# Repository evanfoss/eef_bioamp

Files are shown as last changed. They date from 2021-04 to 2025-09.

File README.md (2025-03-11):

# EEF_BioAmp

This project is a family of differential input amplifiers with single ended outputs for use in electrophysiology. 
They are all *not* rated for use on humans. Let me repeat do not connect this to a person. If you do I am not responsible.

This is a fork of my original work here: https://github.com/EPL-Engineering/epl_bioamp

There are a few versions

EEF BioAmp "Fancy" - (master branch)

EEF BioAmp "Cheap" - (cheap branch)

### EEF BioAmp "Fancy"
The "Fancy" version has every bell and whistle we reasonably expect a user to need for doing ABR, DP, and EKG. Often these users have multiple dedicated amplifiers and prefer to use more involved filtering so that EKG signals can be seperated from ABR and etc for example.
The feature set I have given it so far includes.
* Twinaxial BNC Input
* Coaxial BNC Output
* Gain of 1K/10K or Gain of 10K/100K
* LPF 3KHz/10KHz
* HPF 300Hz 
* Optional the HPF can be 300Hz/10Hz
* Optional Power Line Frequency Rejection (currently 60Hz but I may do 50Hz in the future)
* Optional EPL Subrack Power
* Optional Battery Power

Please Note: The HPF option and Power Line Rejection option are mutually exclusive because of front panel constraints. Likewise the EPL Subrack Power and Battery Power are mutually exclusive because of rear panel space constraints. 

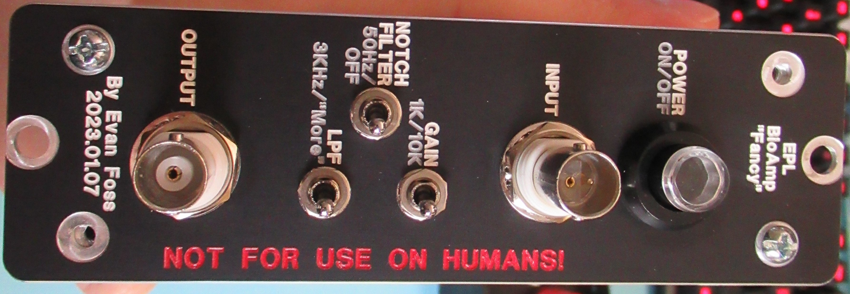
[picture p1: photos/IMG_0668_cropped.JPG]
Front panel of the bioamp.
|
|:---------------
|Pic1: A picture of a BioAmp front panel upclose enclosed in a subrack module.

|Circuitboards for the bioamp inside a chassis.
|:---------------
|Pic2: A picture of inside of an assembled BioAmp.

### EEF BioAmp "Cheap"

<this version is not maintaned currently>

The "Cheap" verion is designed to be pure minimalism. The idea was to have a lower cost version of the fancy that is just for ABR, DP, and EKG measurements. It's meant for our simple dedicated chambers where users exclusively do ABRs all day long with a single BioAmp and never adjust settings. The following is it's configuration.
* Twinaxial BNC Input
* Coaxial BNC Output
* Gain of 10K
* LPF 3KHz
* HPF 300Hz
* EPL Subrack Power
* Optional Power Line Frequency Rejection (currently just 60Hz but again I might add 50Hz later)

Please Note: The Power Line Frequency Rejection in some units is not user adjustable.

### EEF BioAmp "Breakout Pod"

This is shared between the "Cheap" and "Fancy" versions. Like both of them it is not for use on humans. 
It's features include the following.
* Twinaxial BNC Output
* 3 x 5 Way Binding Post Input
* 3 x 1.5mm Male Input (DIN 42802-1 Compatible Connectors)
* Holes on the sides for Mounting to Tables and etc.

The mounting holes are more important than they might sound. In a lot of our booths the EPL Subrack the EPL BioAmp sits in is on a shelf while the subject of the testing is on a sliding optical breadboard.

|5 breakout pods sitting next to each other.
|:---------------
|Pic2: A picture of 5 breakout pods.

# Development

### Toolchain

The development toolchain was as follows:

|Tool Name             | License        | Function
|:---------------      | :------------- | :-----------------
|<a href="https://octave.org/">Octave</a>                                                    | Open Source       | Scientific Programming Language used for calculations
|<a href="https://github.com/lepton-eda/lepton-eda">lepton-eda</a>                           | Open Source       | EDA (Electronic Design Automation) suite lepton-eda a fork of gEDA
|<a href="http://repo.hu/projects/pcb-rnd/">pcb-rnd</a>                                      | Open Source       | CAD (Computer Aided Design) tool for PCB (Printed Circuit Board) layout gEDA/PCB
|<a href="https://gerbv.github.io/">gerbv</a>                                                | Open Source       | Gerber viewer
|<a href="https://www.gnu.org/software/make/">GNU/Make</a>                                   | Open Source       | Toolchain automation
|<a href="https://www.frontpanelexpress.com/front-panel-designer">Front Panel Designer</a>   | Free as in Beer   | Front Panels Express Software

The toolchain automation uses the following commands:

|Command               | Implimented | Operation
|:---------------      | :------------- | :-----------------
|make all               | Yes           | edits Makefile
|make change            | Yes           | edits all projects schematics
|make simulation        | No            | runs spice simulation
|make graph             | Yes           | opens spice simulation graph(s)
|make mainmath          | Yes           | run the numbers for the filter values
|make notchmath         | Yes           | run the numbers for the notch filter option values
|make editmainmath      | Yes           | edit the code for the filter
|make editnotchmath     | Yes           | edit the code for the notch filter
|make pcb               | Yes           | edits bioamp main board pcb
|make pcb2              | Yes           | edits notchfilter option pcb 
|make pcb3              | Yes           | edits highpass filter option pcb
|make gerbv             | Yes           | opens gerber viewer of bioamp main pcb
|make gerbv2            | Yes           | opens gerber viewer of notchfilter pcb
|make gerbv3            | Yes           | opens gerber viewer of highpass filter option pcb

### Design

## Circuit Design

The diagram in Sch0 shows the overall design concept for the fancy version of the BioAmp. 

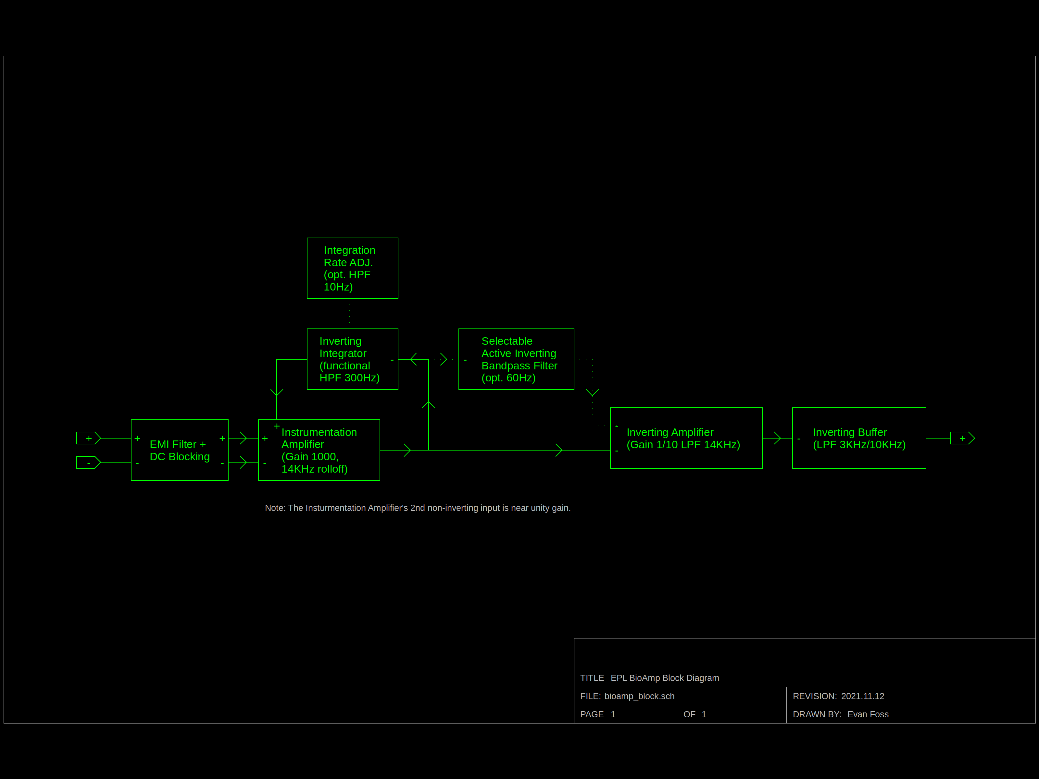
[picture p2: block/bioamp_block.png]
Block diagram of the fancy bioamp.
|
|:---------------
|Sch0: Block Diagram

The mainboard of the BioAmp is made up of the schematics Sch1 & Sch2. The optional Notch Filter board is just Sch3, and the optional highpass filter option is Sch4.

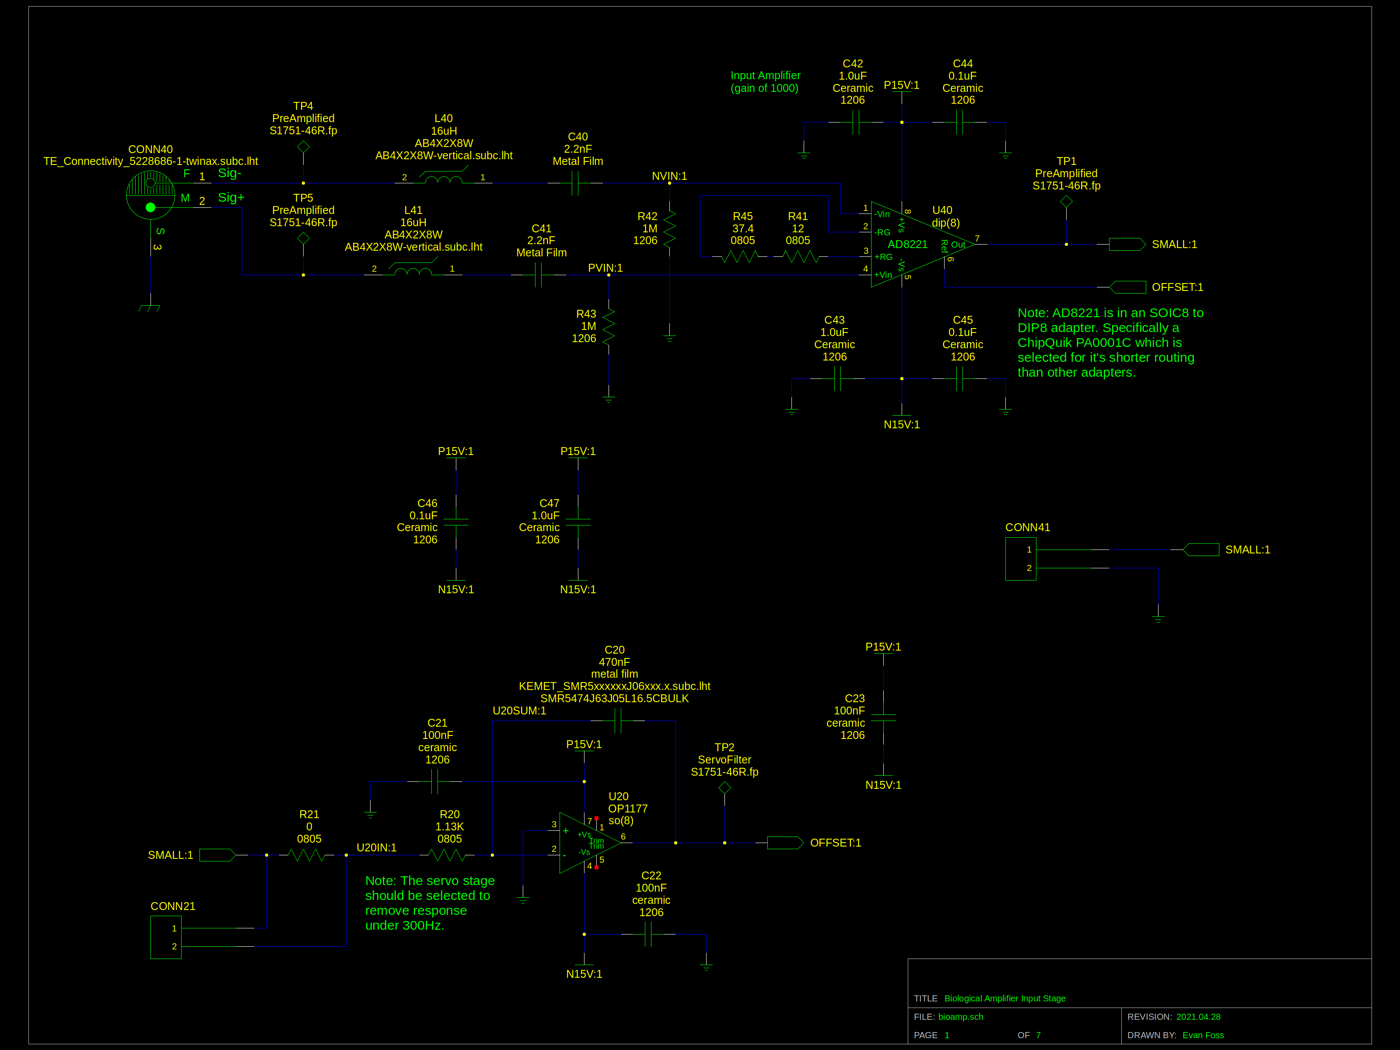
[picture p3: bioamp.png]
Bioamp input stage with integrator schematic.
|
|:---------------
|Sch1: BioAmp Input Stage

Sch1 shows the input filter composed of L40, L41, C40, C41, R42, and R43.

Sch1 also includes the insturmentation amplifier is U40, and it's gain limits it's frequency response. The gain for this stage is set by R45 + R41. It has the usual capacitors sprinkled around it for power supply decoupling.

U40 was selected for it's ability to operate at high gain with relatively low noise, and a level of input offset that could be overcome with an integrator. 

The inverting integrator which acts as a low pass filter is built around U20. R20 and C20 set the time constant for the integration. R21 and the jumper over it are for adjusting this lower limit if the highpass filter adjustment option is installed. 

U20 was selected for it's lower input bias current, low input offset voltage, and of course to drive a capacitive load. C20's composition was selected for low dielectric absorbtion. The same reasoning was used for C40, and C41. Dielectric absorbtion in C20 would lead the integrator to drifting and in C40 or C41 it would lead to the input stage having issues with input bias voltage.

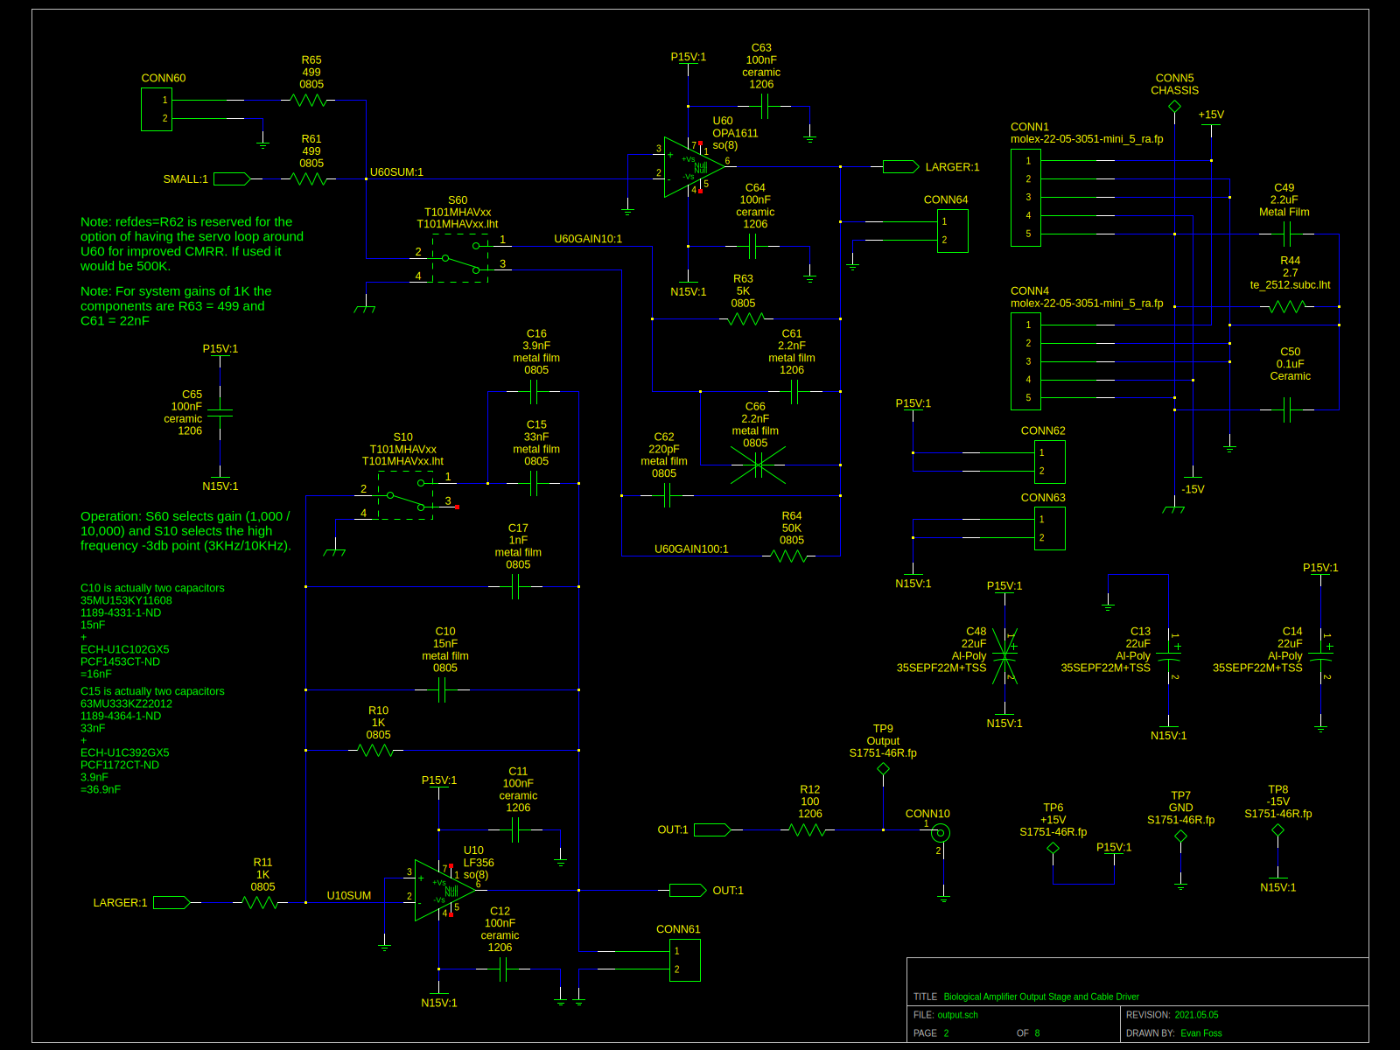
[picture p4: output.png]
Bioamp output stage schematic.
|
|:---------------
|Sch2: BioAmp Output Stage

Sch2 starts with the inverting amplifier that adds the rest of the gain required. It has 2 inputs. The 1st input is from the input stage on Sch1 and the 2nd is for the notch filter option. S20 selects the feedback RC pair (R63 & C61) or (R64 & C62). 

The use of the OPA1611 here is excessive considering it's performance characteristics but please see the note in "Supply Chain Issues". However it is very low noise in this application. 

In Sch2 we also have the final output stage which is built around U10. It is setup to just invert the signal at unit gain. The switch S10 adds added capacitence across the feedback resistor R10. Obviously R10 and R11 should match each other for this to work. C10+C17 put a limit on the frequency response. C16+C17 add more capacitence to lower the frequency response even more.

Once more to control noise the chassis ground is connected to the exterior of the switches S20 and S10 so that it can connect through them to the chassis.

Grounding gets complicated. Every amplifier in the chamber would work best if it was the only place were chassis ground and analog common were connected. That connection improves performance but you can't do that because of the ground loops it would add. That is why I now believe the over all enclosure (subrack/multiamplifier chassis) *or* the most sensitive/critical amplifier should be where that connection happens. Following that logic the next best thing we can do for each amplifier is to add an RC bridge between chassis and analog common. The 2.7 Ohm resistor is enough that it's not technically a "loop" and also small enough that the safety of a possible split where ever the chassis / common connection won't put the user in an unsafe situation. (but that should *never* *ever* happen!) Everyone repeat after me "I will never unground a chamber."

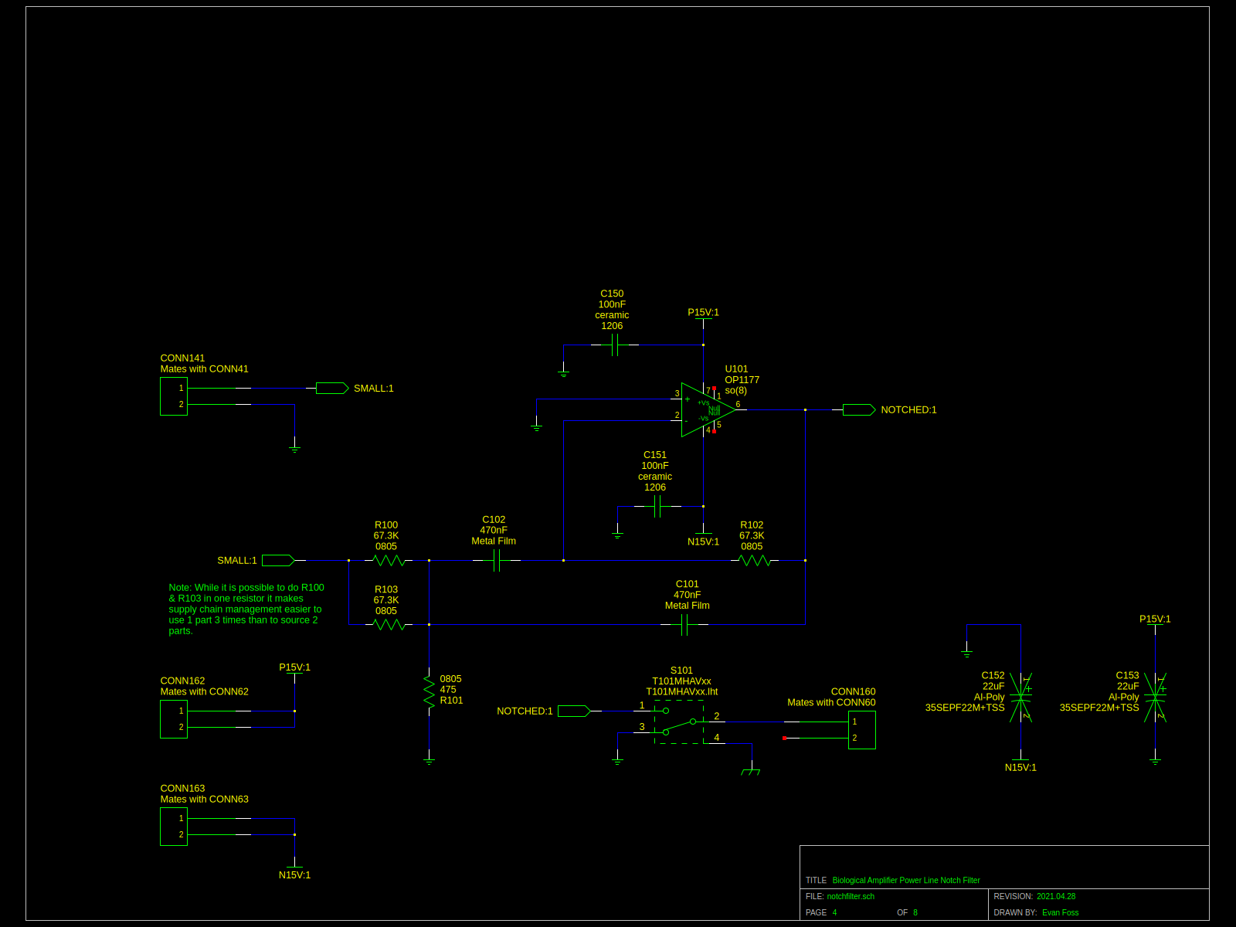
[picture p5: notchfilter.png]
Notch filter option schematic.
|
|:---------------
|Sch3: Notch filter option

The notch filter shown in Sch3 is built around U101. It works as an inverting unity gain filter. That way the inverted signal can be added back into the main device at cancel out the offending frequency. Normally this would cause phase issues but the frequency in question is 60Hz (or with changes 50Hz).

U101 was selected using the same criteria as U20 on Sch1 as a result the same part was selected. I should really say I picked this topology so I could use the same opamp and the same value for C101 and C102 as I did in C20. The catch is that C101 and C102 require a level of tollerance that C20 does not because the notch filter's performance is tied to the matching of these parts.

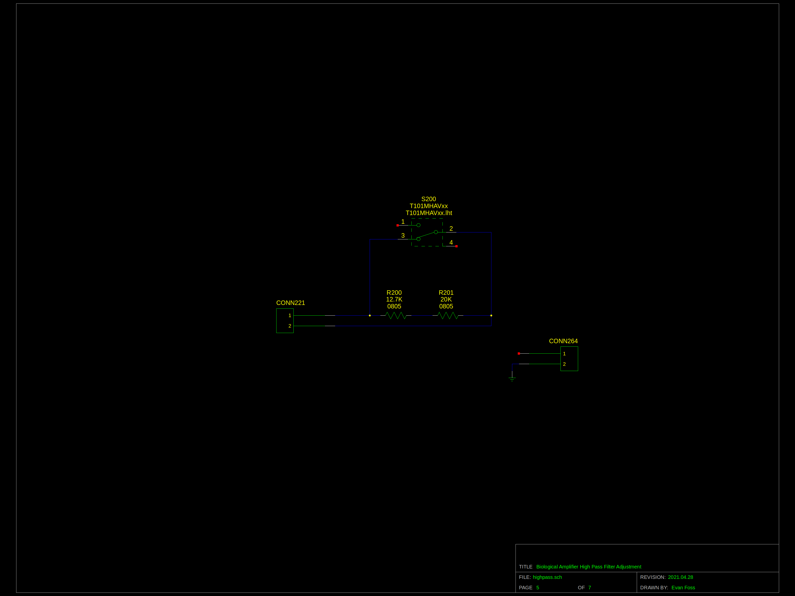
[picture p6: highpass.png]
Highpass filter lower frequency option schematic.
|
|:---------------
|Sch4: Highpass filter lower frequency option

Sch4 just optionally adds resistance in the integrator in Sch1 slowing down it's integration rate and lowering the input stage's highpass filter to 10Hz.

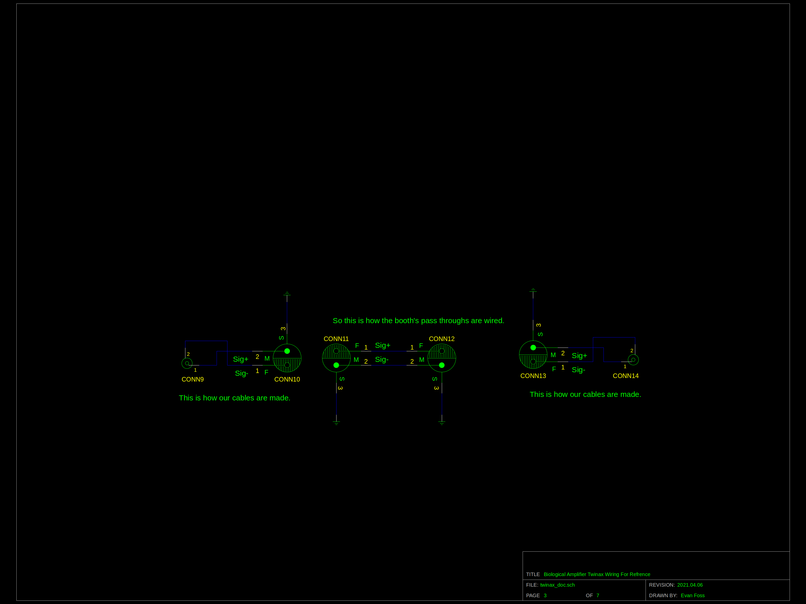
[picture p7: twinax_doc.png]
Schematic documenting the way twinaxial coax flips polarity from device to cable and back.
|
|:---------------
|Sch5: Twinaxial coax flips documented

Sch5 just helps you understand the polarity of the signal as it goes through the twinaxial wiring.

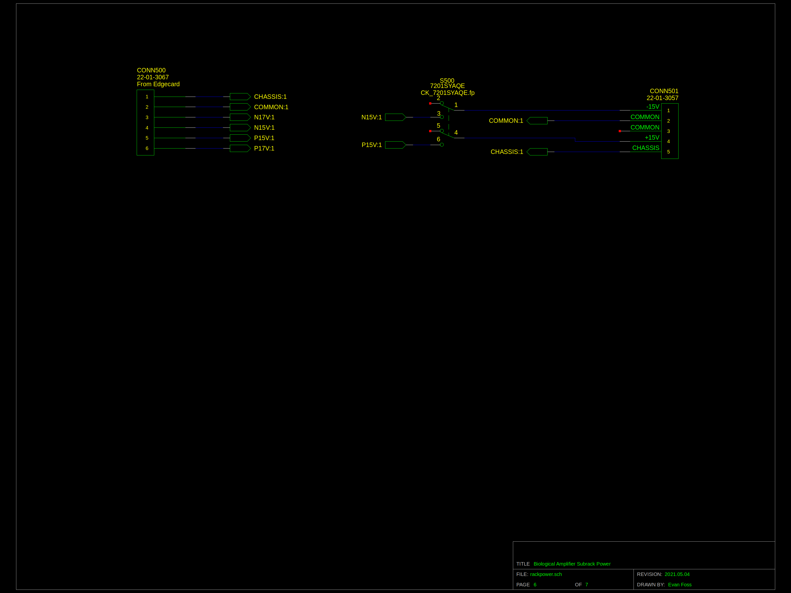
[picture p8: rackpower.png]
Rack based power schematic.
|
|:---------------
|Sch6: Rack based power option

Sch6 really is what it says.

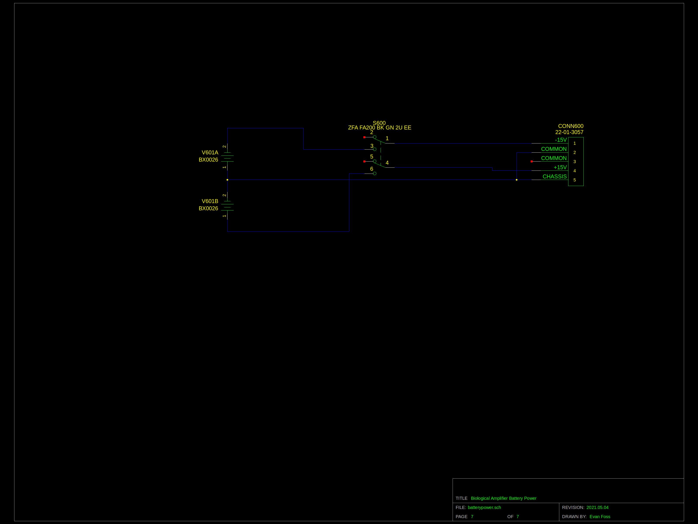
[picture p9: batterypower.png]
Battery based power schematic.
|
|:---------------
|Sch7: Battery based power option

Sch7 like Sch6 is exactly what it says. The one complication is that as this is the "only device" on this power supply it has to be where the analog common and chassis ground are connected.

## Printed Circuit Board Layout

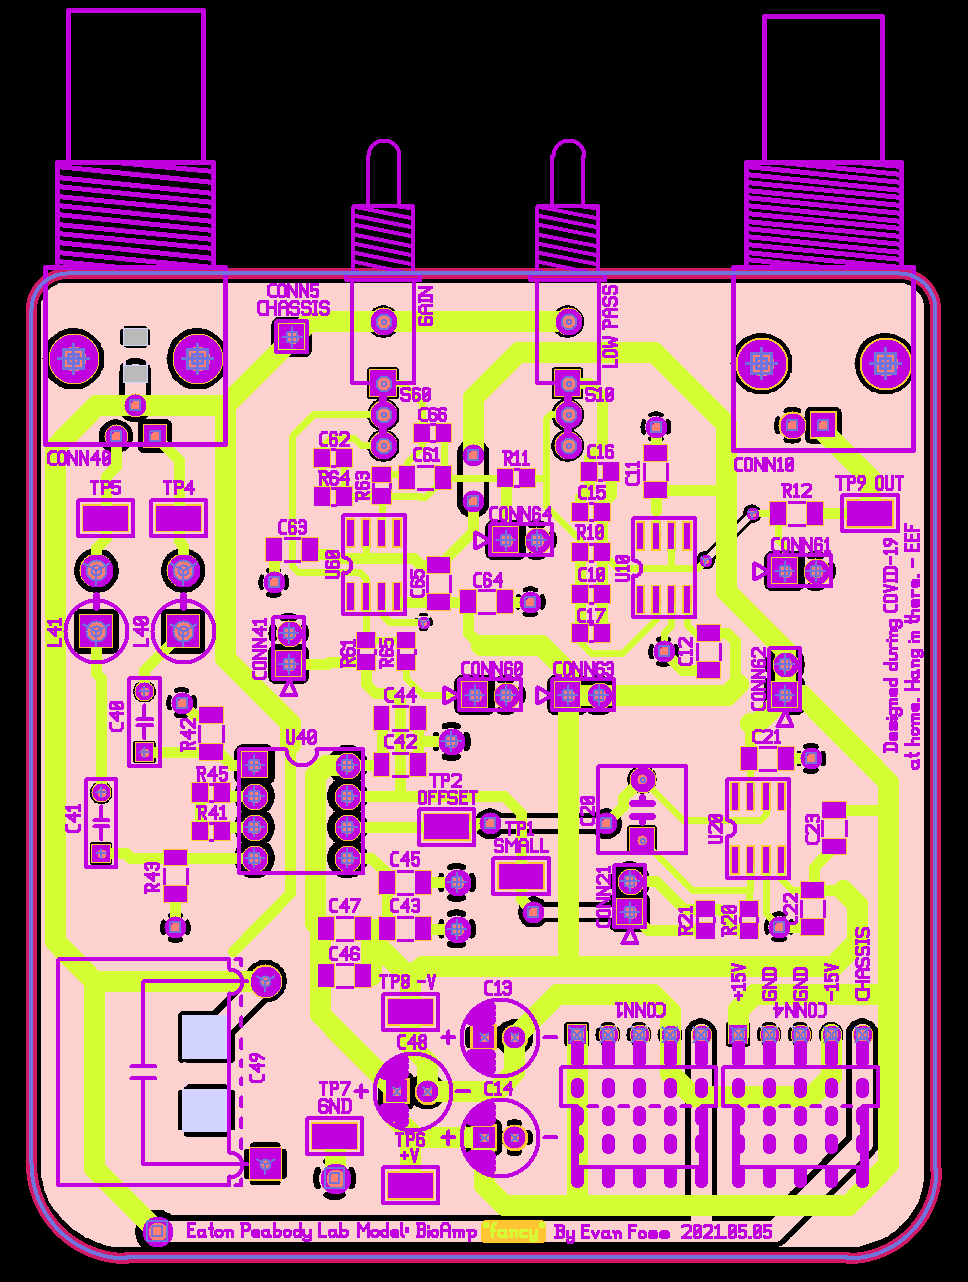
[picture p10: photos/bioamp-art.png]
Image of the main BioAmp PCB rendered by the gerber viewer in neon colors.
|
|:---------------
|PCB1: Image exported from the gerber viewer of the main BioAmp circuit board layout

One more thing about U40. Although it has yet to happen I believe this is the part most likely to be toasted by static discharge as it is the most directly connected to the user touchable connections. This is why it's on a small SOIC to DIP adapter. It is a method of reducing downtime from repairs. 

The layout was obviously designed to have the feedback paths as short as was reasonably possible. The decoupling capacitors were also kept close to the pins of the opamps they were meant to be near. Some effort was put into making sure the input side of the insturmentation amplifier was kept away from the rest of the design to avoid coupling anything over.

I sprinkled in a liberal number of test points so that repairs and debuging would be easier. 

The layout was drawn to be inside this size onvelope based on the packaging plan I had. For more on that see "Packaging".

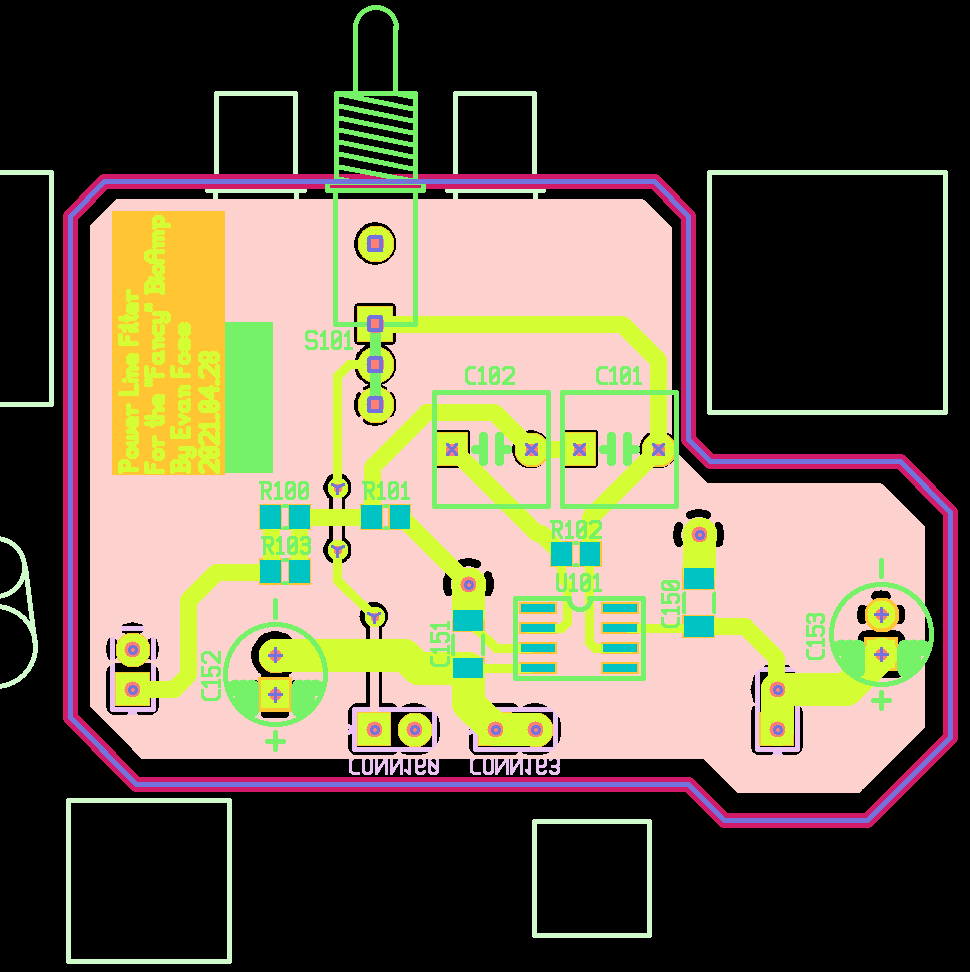
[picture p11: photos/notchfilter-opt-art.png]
Image of the Notch Filter PCB rendered by the gerber viewer in neon colors.
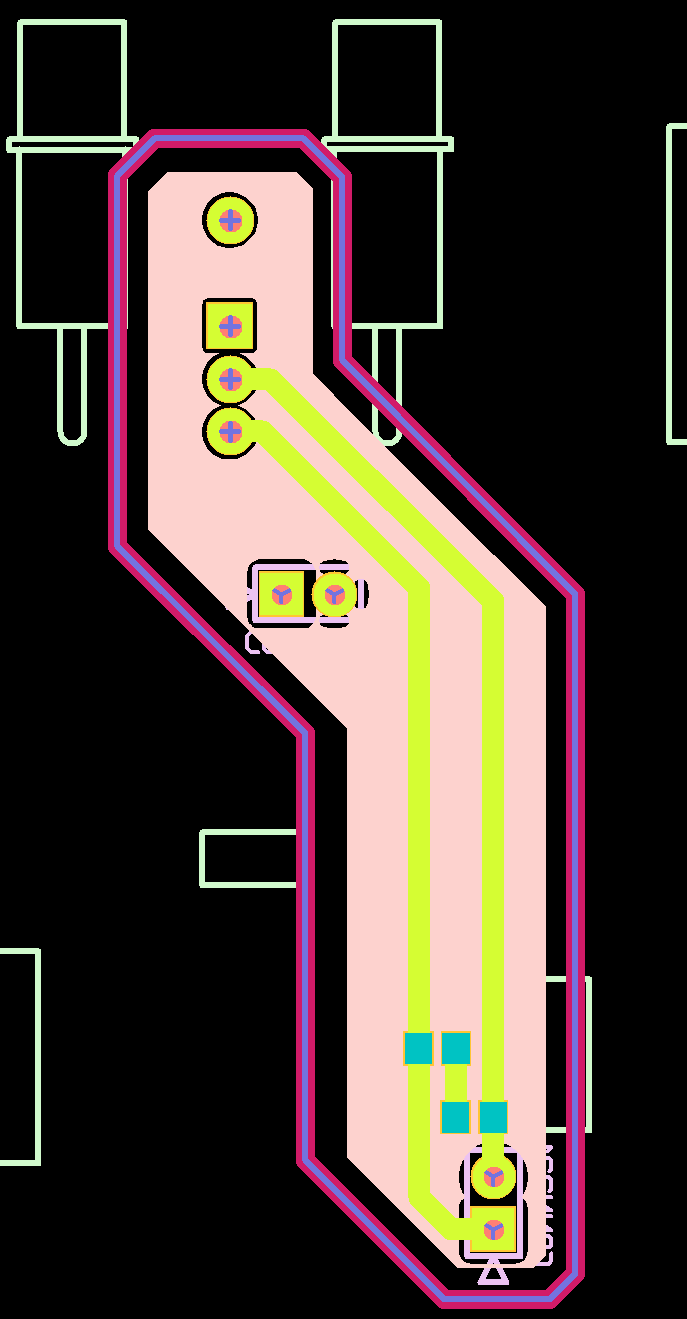
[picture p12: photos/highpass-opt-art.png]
Image of the High Pass Filter Adjustment Option PCB rendered by the gerber viewer in neon colors.
||
|:---------------                                   |:---------------
|PCB2: Notch Filter Option PCB Layout.                     |PCB3: Low Pass Filter Adjustment Option PCB Layout.

### Packaging

The BioAmp was designed with a few packaging options in mind. The image at the top of the README is of the front panel for a subrack module but it was also planned to be included in a standard 19" equipment/"server" rack package U1 size enclosure. The idea was to package it with the other hardware commonly used in the chamber for doing ABR (Auditory Brainstem Response) testing.

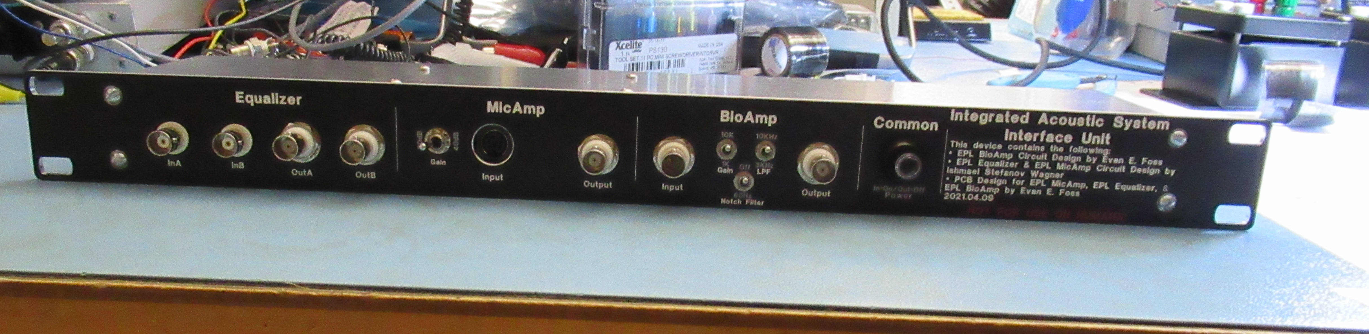
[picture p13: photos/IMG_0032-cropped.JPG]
Image of the combined front panel for the integrated bioamp with mic amp and equalizer.
|
|:---------------
|Pic3: Front panel of an integrated device with a <a href="https://github.com/evanfoss/eef_micamp">Mic Amp</a>, <a href="https://github.com/evanfoss/eef_equalizer">Equalizer</a> and BioAmp all in a U1 enclosure.

That said I prefer the subrack module packaging shown at the opening of the readme in Pic1 because of the other modules that fit neetly in the subrack.

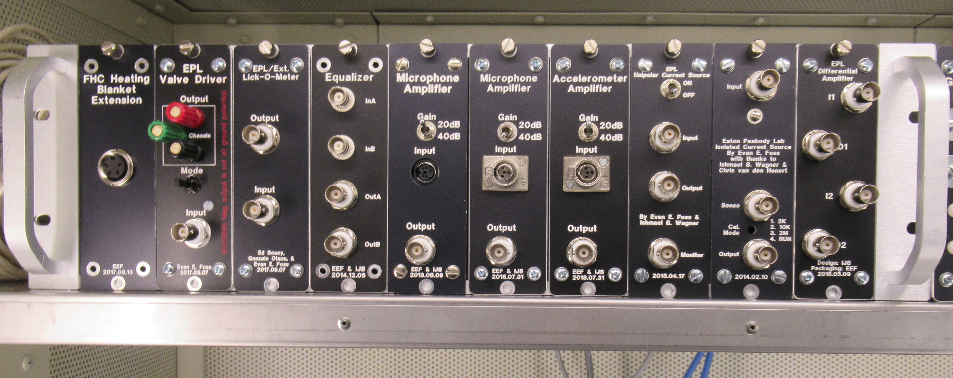
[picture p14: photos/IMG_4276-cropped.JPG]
Image of the subrack holding other modules that go in the rack
|
|:---------------
|Pic4: An array of just some of the many subrack modules that could be used in parallel to the BioAmp.

Outside of EPL of course this level of flexibility is in low demand.

The other big demand is of course battery powered operation. Now I frown on it because of the environmental footprint of batteries but there is a rear panel design that is included in the project files. Some thought went into the selection of the battery holder to make ease of changing the batteries without opening the cover easier. I find those little vinyl enclosed snap on 9V connectors unpleasant. The holder I selected costs a lot more but it works very well, the covers are hard to loose, and in most cases they make it impossible to put the batteries in backwards. 

The power button assembly was picked both because the on/off state was clearly visible without power but also because some experiments require low to zero illumination so power indicator lights are frowned appoon. I had a project with optogenetics and a blue power indicator in a commericially made device was causing trouble.

The breakout pod (Pic2) was designed in because many users require the chamber table to be at a distance from the equipment rack or for ergonomic reasons they need a chamber to have a pull out tray. So connecting the electrodes to the BioAmp front panel directly was not advisable.

### Manufacturing

Initial prototypes were made with hand soldering under a microscope. However I prefer to build these in batches which makes using solder paste nessisary. 

#### Reflow Soldering

With the switch to reflow soldering I had to switch to solder paste. Because solder paste has to be washable in this case the flux was going to dry out and I worried about the fine metal balls in the suspension were going to become a safety concern. This required the change to lead free solder to reduce exposure risk.

This is my current assembly process:

0. Verify that all parts are on hand including front panel
1. Stencil on solder paste
2. Apply SMT components
3. Warm the PCBA on a hot plate
4. Reflow PCBA
5. Ramp PCBA temperature down
6. Solder all through hole components except the switches and connectors
7. Insert switches and connectors and fasten them to the front panel (finger tight)
8. Solder switches and connectors
9. Detach front panel from PCBA
10. Wash PCBA and front panel seperatly
11. Check PCBA under microscope and record assembly with pictures
12. Assemble PCBA into chassis and test

|Populated ciruitboards for the bioamp.
|:---------------
|Pic5: Populated BioAmp main circuit board and notch filter option board on the right.

#### Supply Chain Issues

The Input stage IC AD8221 was selected before the COVID-19 pandemic and tarif issues made the supply chain for it an issue for me. The higher quality bin of the part (lower input offset rating) has at times been hard to keep instock. Likewise the capacitors used for limiting bandwidth in the stages of Sch2 are also an issue but I resolved that by adding pads for other packages in parallel.

The performance of the device in it's first prototypes (late 2020/early 2021) and the later itterations have drifted a bit. I believe this maybe do to variations in the process control of some parts. This is why the 10KHz LPF (Low Pass Filter) option is now marked as "More". I don't like it but as this feature is almost never used by 90% of users it for more than debugging test chamber noise restoring this to a known 10KHz is not a priority.

The OPA1611 was used because it was thought at the time that it would be used in later itterations of the MicAmp and that consolidation of the parts lists would help make stocking parts easier. In reality the testing of that which was concurrent with the testing of this project showed that it was a bad idea but the part is stocked now. It would have been nice if TI had not ceased production of the LME49710 so both designs could have used that part. *grumbles*

The notch filter requires on obscure part 67.3K Ohm resistors ideally in 1% or better tollerance. I resolved this issue by buying in large quantity.

To simplify the front panel design and supply chain issues I used the same model switch for everything.

The front panel twinaxial connector that is PCB mount and right angle is no longer manufactured. However it is still commonly available on the surplus market. The non-PCB mount version is also still common so you can buy those and solder wires to the PCB.

Finally some readers might notice that I used 22uF aluminum polymer capacitors instead of tantalum or ceramic. I stopped using tantalum and most ceramic because of the conditions around <a href="https://www.wbur.org/npr/1152893248/red-cobalt-congo-drc-mining-siddharth-kara">mining used in their production.</a> Ceramic capacitors were also avoided in many locations because of their microphonic effects <a href="https://product.tdk.com/system/files/contents/faq/capacitors-0031/singing_capacitors_piezoelectric_effect.pdf">caused by piezoelectric effects.</a>

### Validation

Validation was done by me at home with a homemade attenuator and my HP35665A and then repeated independently by Ishmael S. W. at EPL using the shop PXI and it's PXI4461 DAQ card before the BioAmp was released to the users. The first 3 or 4 users were also told to repeate the tests of frequency reponse and gain and found it proper for use in ABR (auditory brainstem response) measurement. For every unit I have made since these tests have been repeated with the HP35665A and cross checked against the original results for consistancy. Later it was suspected by me that the 10KHz option might infact be landing lower than 10KHz and so the feature was depreciated to "More" on the control panel. I bought a brand new Keysight U1733P and tested all the capacitors etc in one unit but could not find a suitable drift in component value to explain it. I had thought the soldering process revisions might be causing values to drift. More on this in the heading "Future".

### Testing

The use of an attenuator is required with the HP35665A as the input voltage range is so small all direct output settings from the DSA (Dynamic Signal Analyzer) would be too large. The attenuator's issues could actually be the cause of the LPF 10Hz issue.

Of the dozen or so units I made only a few were notably out of spec to the point where the capacitors (often tolleranced at 2% or better) needed to be swapped to meet requirements. This most commonly happened in the 60Hz notch filter where the parts exact rating doesn't matter as much as their matching which is harder to assure without an unreasonably high BOM price.

### Maintence and Errata

* 2021 - One unit destroyed when the user installed the batteries backwards frying most of the IC's inside. Additional labeling was added to the sides indicating battery alignment.
* 2022 - Added extra footprint for alternative package size C66 to replace C61
* 2025.03.10 - 3 Units (1 @ EPL, 1 @ _Unanmed_Biotech_Startup_, 1 @ Baylor) stopped operating until they were powered off and their inputs shorted temporarily.  Writing this documentation caused me to catch that I had listed the wrong composition for C40 & C41 in the BOM. Looking at that made me realize that the lockup issue was likely caused by those parts accumulating a charge. Normally the impedance to the refrence electrode would be on the order of 20K Ohms which should keep it discharged but I suspect over time charge is allowed to accumulate. I have a suggested correction. I would prefer 1.1nF instead of 1.2nF (1.1nF would hold the -3dB point @ 7.2343 Hz vs 1.2nF which puts it at 6.6315 Hz) however 1.1nF parts are not commonly available.

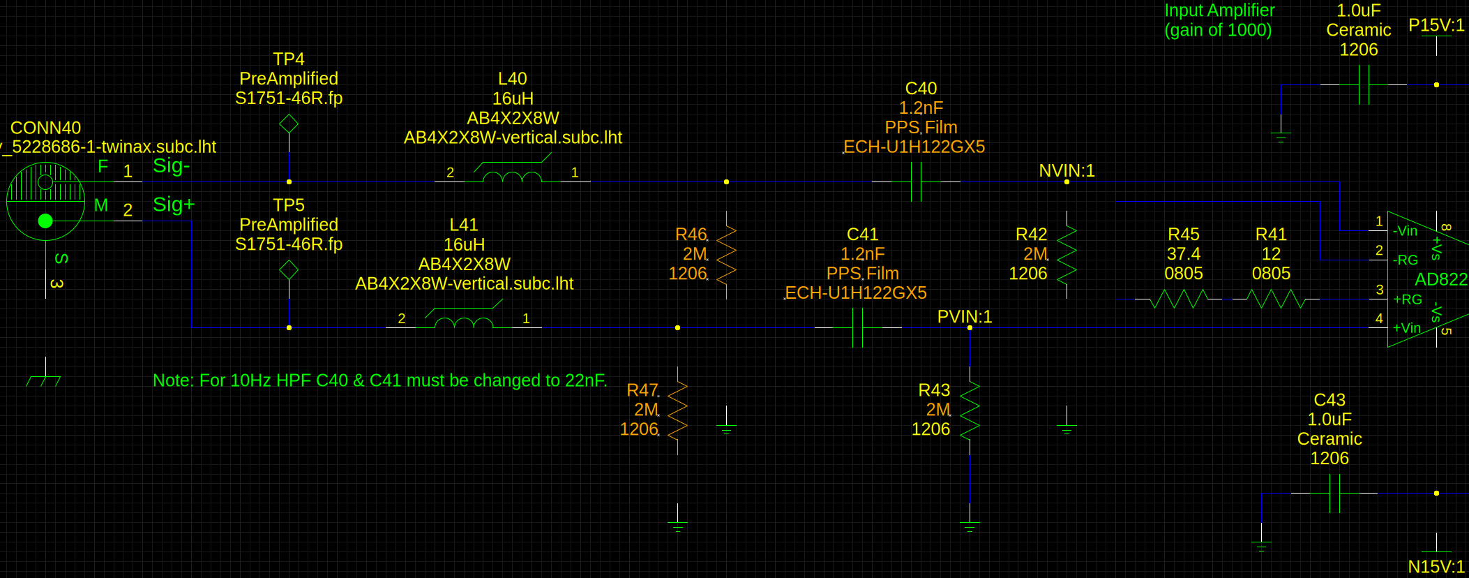
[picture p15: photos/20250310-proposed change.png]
revised schematic
|
|:---------------
|ALT1: I highlighted the changes. I am suggesting adding 2 more resistors before the input filter capacitors but after the inductors and changing the capacitors to PPS film (1.2nF) and the resistors 2M Ohm.

   Or we could just tell users to leave the + electrode in the 5 way - binding post top or vice versa between uses. As all three incidents happened multiple years into use this seems excessive.
   Another good option is to give users a small block of antistatic foam to squeeze between the 5 way binding posts and to tell them to insert the needles into that between uses.

* 2025.03.11 - I noticed there were some parts that I have never deliberately stuffed on the PCB's so I revised the schematics.

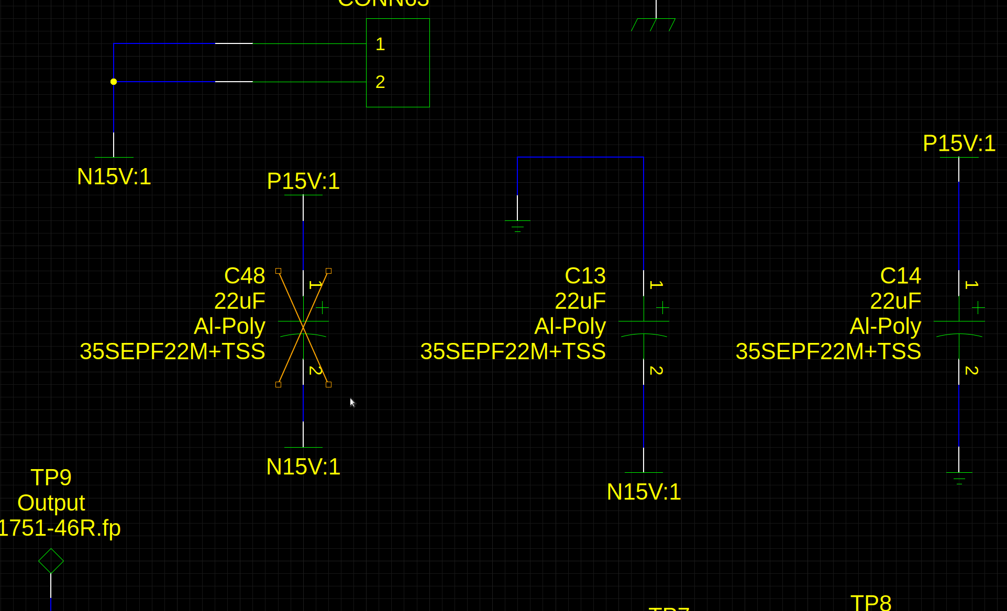
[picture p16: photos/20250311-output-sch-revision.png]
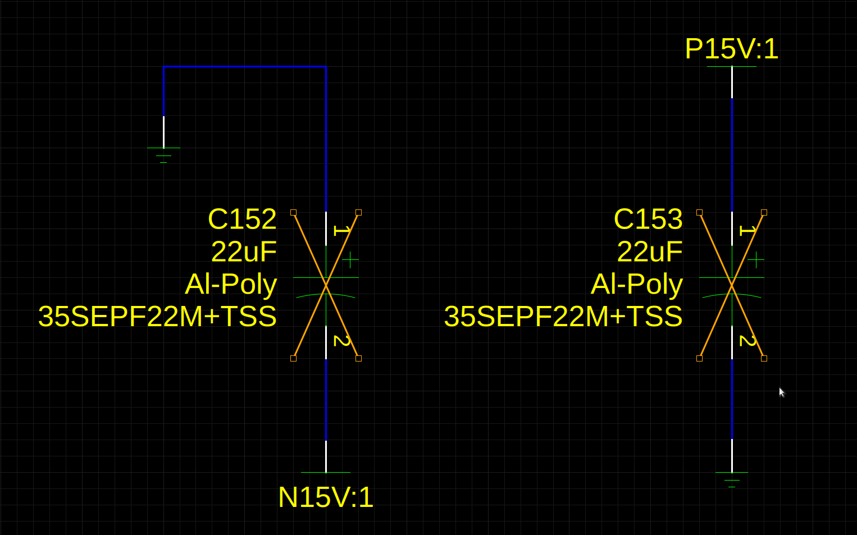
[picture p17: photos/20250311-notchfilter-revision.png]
||
|:---------------                               |:---------------
|ALT2: output.sch C48 is not to be stuffed      |ALT3: notchfilter.sch C152 & C153 are also not stuffed

## Changelog

### Post EPL fork

2022 - Revised output.sch to add extra footprint for 2nd package size of C66 to replace C61 if unavailable.

2025.03.07 - Improved README.md with images of the schematics and some initial added text

2025.03.08 - Rewritten notes into proper matlab/octave code for the BioAmp filter components

2025.03.10 - Correction/Fix to bill of matterials (bom.txt) about C40, C41 composition. Now actually PPS film for reduced dielectric absorbtion.

2025.03.11 - Added documentation in errata & fixed automatic gerber export

## Future

* Migration off the old gsch2pcb-rnd script which is depreciated in modern releases of pcb-rnd
* Spice Simulation of the design complete with an estimated source model.
* Refining the 10KHz mode or settling the uncertanty would be nice. 
* A more refined attenuator for testing without a PXI.

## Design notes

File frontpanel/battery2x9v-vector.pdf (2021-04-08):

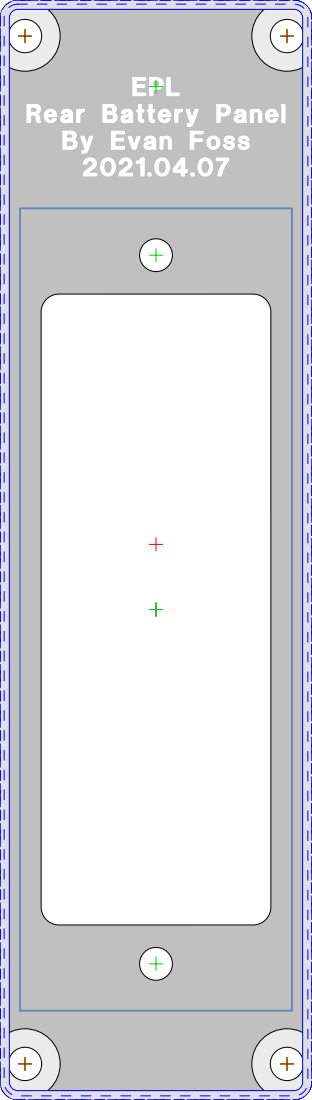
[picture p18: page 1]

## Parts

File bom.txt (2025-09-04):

EPL BioAmp Fancy
Parts List
bom.txt
By Evan Foss
2021.04.30

The following is a work in progress

BioAmp "Fancy" - Common Parts
Quant.	Model#			Distributor	Distributor#			Value	Description
1	AD8221BRZ		Digikey		AD8221BRZ-ND			N.A.	Insturmentation Amplifier 8 SOIC Package
1	OP1177			Digikey		OP1177ARZ-ND 			N.A.	OpAmp
1	OPA1611			Digikey		296-47811-1-ND			N.A.	OpAmp
1	LF356			Digikey		LF356MX/NOPBCT-ND		N.A.	OpAmp
1	PA0001C			Digikey		315-PA0001C-ND			SO8	SO8 to DIP8 Adapter
1	110-43-308-41-001000	Digikey		ED90032-ND			DIP8	DIP8 Socket
1	N.A.			Digikey		N.A.				0	Resistor 0805 Footprint (or a solder bridge)
1	RMCF2512JT2R00		Digikey		RMCF2512JT2R00CT-ND		2	Resistor Footprint 2512
1	ERA-6AHD120V		Digikey		P123888CT-ND			12	Resistor 0805 Footprint
1	ERA-6AHD37R4V		Digikey		P37.4BPCT-ND			37.4	Resistor 0805 Footprint
1	RNCP1206FTD100R		Digikey		RNCP1206FTD100RCT-ND		100	Resistor 1206 Footprint
2	RNCP0805FTD499R		Digikey		RNCP0805FTD499RCT-ND		499	Resistor 0805 Footprint
2	RN73H2ATTD1001B25	Digikey		2019-RN73H2ATTD1001B25CT-ND	1K	Resistor 0805 Footprint
1	RT0805DRE071K13L	Digikey		311-2803-1-ND			1.13K	Resistor 0805 Footprint
2	RT1206FRE071ML		Digikey		YAG5985CT-ND			1M	Resistor 1206 Footprint
1	ECH-U1H102JX5		Digikey		PCF1328CT-ND			1nF	Capacitor Metal Film 0805 Footprint
2	SMR5222J63J01L16.5CBULK	Digikey		399-13049-ND			2.2nF	Capacitor Metal Film PPS Through Hole
1	ECH-U1C392GX5		Digikey		PCF1172CT-ND			3.9nF	Capacitor Metal Film 0805 Footprint
1	35MU153KY11608		Digikey		1189-4331-1-ND			15nF	Capacitor Metal Film 0603 Footprint
1	63MU333KZ22012		Digikey		1189-4364-1-ND			33nF	Capacitor Metal Film 0805 Footprint
12	C1206C104K5RAC7800	Digikey		399-C1206C104K5RAC7800CT-ND	0.1uF	Capacitor Ceramic 1206 Footprint 50V
1	SMR5474J50J04L16.5CBULK	Digikey		399-13063-ND			0.47uF	Capacitor Metal Film PPS 5% 50VDC
3	CL31B105KBHNFNE		Digikey		1276-3091-1-ND			1uF	Capacitor Ceramic 1206 Footprint
2	ECQ-E1225KF		Digikey		EF1225-ND			2.2uF	Capacitor Metal Film 10% 100VDC
2	35SEPF22M+TSS		Digikey		P16407CT-ND			22uF	Capacitor Aluminum Polymer 20% 35V
2	AB4X2X8W		Digikey		AB4X2X8W-ND			8mm_2mm	Ferrite Bead
9	S1751-46R		Digikey		952-1478-1-ND			N.A.	Test Point
7	929647-09-02-I		Digikey		3M156537-02-ND			2Pos	Connector Male 2 Position 0.1" Spacing Gold Plating
2	T101MHAVBE		Digikey		CKN9899-ND			SPDT	Switch SPDT 0.4VA 20V Chassis GND Pin Toggle Switch Right Angle+PCB Mount Vertical Actuator
2	22-05-3051		Digikey		WM4303-ND			5Pos	Connector 5 Position Right Angle 0.1" Spacing Ramp and Rib Locking
1	031-5431-10RFX		Digikey		ARF1690-ND			N.A.	Connector BNC Right Angle+PCB Mount Includes Mounting Hardware
1	5228686-1		Digikey		A32412-ND			N.A.	Connector Twinax BNC No Included Mounting Hardware
1	031-5653		Mouser		523-31-5653			N.A.	1/2" Diameter Lockwasher
1	031-5652		Digikey		ARF1927-ND			N.A.	1/2"-28 Nut
1	EFP164A97F		Digikey		EFP164A97F-ND			N.A.	Subrack Module Chassis

BioAmp "Fancy" - 1K/10K Gain
1	RNCP0805FTD499R		Digikey		RNCP0805FTD499RCT-ND		499	Resistor 0805 Footprint
1	RNCP0805FTD4K99		Digikey		RNCP0805FTD4K99CT-ND		4.99K	Resistor 0805 Footprint
1	ECH-U1H222JX5		Digikey		PCF1332CT-ND			2.2nF	Capacitor 0805 Footprint
1	FCP1210H223J-G2		Digikey		338-4085-1-ND			22nF	Capacitor 1210 Footprint

BioAmp "Fancy" - 10K/100K Gain
1	RNCP0805FTD4K99		Digikey		RNCP0805FTD4K99CT-ND		4.99K	Resistor 0805 Footprint
1	RNCP0805FTD49K9		Digikey		RNCP0805FTD49K9CT-ND		49.9K	Resistor 0805 Footprint
1	ECH-U1H221GX5		Digikey		PCF1288CT-ND			220pF	Capacitor
1	ECH-U1H222JX5		Digikey		PCF1332CT-ND			2.2nF	Capacitor

BioAmp "Fancy" - Option Notch Filter 60Hz
1	OP1177			Digikey		OP1177ARZ-ND			N.A.	OpAmp
1	ERA-6AEB4750V		Digikey		P475DACT-ND			475	Resistor 0805 Footprint
3	RN732ATTD6732B25	Mouser		660-RN732ATD6732B25		67.3K	Resistor 0805 Footprint
2	C1206C104K5RAC7800	Digikey		399-C1206C104K5RAC7800CT-ND	0.1uF	Capacitor Ceramic 1206 Footprint
1	SMR5474J50J04L16.5CBULK	Digikey		399-13063-ND			0.47uF	Capacitor Metal Film PPS 5% 50VDC
1	T101MHAVBE		Digikey		CKN9899-ND			SPDT	Switch 0.4VA 20V Chassis GND Pin Toggle Switch Right Angle+PCB Mount Vertical Actuator
4	929850-01-02-RA		Digikey		929850E-01-02-ND		2 Pos	Connector Female 2 Position 0.1" Spacing Gold Plating

BioAmp "Fancy" - Option Notch Filter 50Hz
This needs to be worked out.

BioAmp "Fancy" - Option HPF 10Hz/300Hz
1	ERA-6AEB1272V		Digikey		P12.7KDACT-ND			12.7K	Resistor 0805 Footprint
1	RNCP0805FTD20K0		Digikey		RNCP0805FTD20K0CT-ND		20K	Resistor 0805 Footprint
1	T101MHAVBE		Digikey		CKN9899-ND			SPDT	Switch SPDT 0.4VA 20V Chassis GND Pin Toggle Switch Right Angle+PCB Mount Vertical Actuator
2	929850-01-02-RA		Digikey		929850E-01-02-ND		2 Pos	Connector Female 2 Position 0.1" Spacing Gold Plating

BioAmp Breakout Pod
1	AN-2851-AB		Digikey		377-2363-ND				Box Hammond Diecast Aluminum Powder Coated
1	31-223			Digikey		ARF1038-ND				Twinax Connector Panel Mount (expensive version)
1	162109			Digikey		ACX2067-ND				Twinax Connector Panel Mount (cheap version)
1	9-227260-0		Digikey		A33796-ND				BNC Lockwasher with Solder Lug
1	111-0104-001		Digikey		J371-ND					5 Way Binding Post (Green)
1	111-0103-001		Digikey		J165-ND					5 Way Binding Post (Black)
1	111-0102-001		Digikey		J164-ND					5 Way Binding Post (Red)
3	140420			Natus		140420					Safelead Adapters (modified see note)
2											4-40 Screws Binding Head
2											#4 Lockwashers
2											4-40 Nuts
1											Wire Stranded Red
1											Wire Stranded Black
1											Wire Stranded Green
1	CTC-5			L-Com		CTC-5					Twinax to Twinax Cable Shielded Twisted Pair

BioAmp - Front Assembly
1	Front Panel
1	ZFA FA200 BK GN 2U EE	Digikey		CKN10064-ND			DPDT	Switch DPDT Push Button Locking Right Angle Mount Mechanical Indicator Solder Eyelet

When ordered individually the switch cap is F11010108	CKN10073-ND

Subrack Module Edgecard - Rear Assembly
1											Rear Panel
1				Digikey							6 Position Right Angle 0.1" Spacing Connector Male

Subrack Module Edgecard - Wire Harness
1	22-01-3067		Digikey		WM2004-ND				6 Position Connector Female Housing
1	22-01-3057		Digikey		WM2003-ND				5 Position Connector Female Housing
1	
10	08-55-0102		Digikey		WM2312-ND		Connector Pin	Connector Crimp Pin Gold Plated (Selective Flash)
1									22AWG		Wire Blue
1									22AWG		Wire Yellow
1									22AWG		Wire Green
1									22AWG		Wire White

Dual 9V Power Supply - Rear Assembly
1											Rear Panel
1	BX0026			Digikey		708-1405-ND				2x 9V Battery Holder

Dual 9V Power Supply - Wire Harness
6	08-55-0102		Digikey		WM2312-ND		Connector Pin	Connector Crimp Pin Gold Plated (Selective Flash)
2	22-01-3057		Digikey		WM2003-ND				5 Position Connector Housing
1				Digikey					22AWG		Wire Blue
1				Digikey					22AWG		Wire Yellow
1				Digikey					22AWG		Wire Green
1				Digikey					22AWG		Wire White

Spair Parts
1	464900201		Digikey		CKN10315-ND	10-48 Nut		T101MHAVBE HDWR SW HEXNUT 10-48 BUSHING 
1	465000201		Digikey		CKN10313-ND	10-48 Bushing		T101MHAVBE SPST Switch Locking Ring (anti-rotation)
1	465200202		Digikey		CKN10314-ND	10-48 Lockwasher	T101MHAVBE HDWR SW LOCK WASHR 10-48 BUSHING

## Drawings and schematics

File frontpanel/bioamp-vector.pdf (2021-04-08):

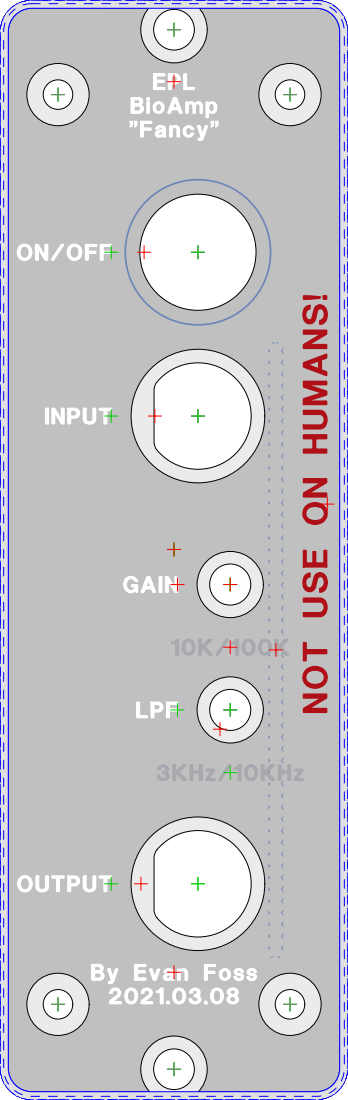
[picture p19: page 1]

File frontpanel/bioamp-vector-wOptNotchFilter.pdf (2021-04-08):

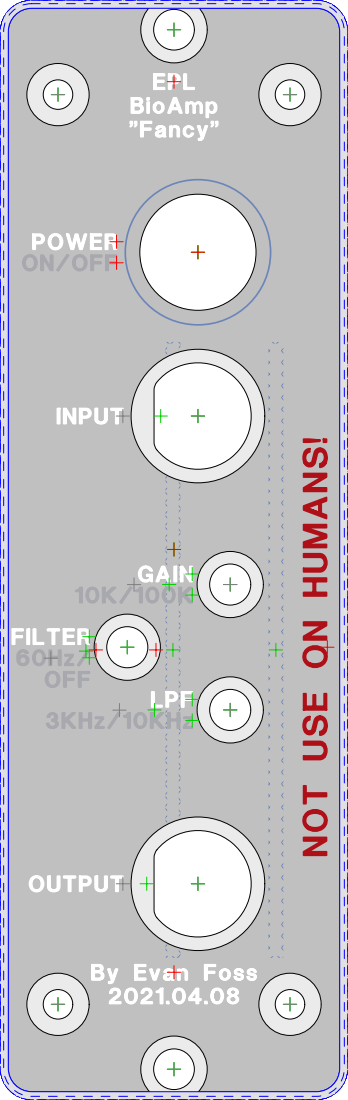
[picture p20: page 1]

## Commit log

2019-01-25 files for prototype
    [AMPHENOL_BNC_31-5431.bottom.gbr, AMPHENOL_BNC_31-5431.bottommask.gbr, AMPHENOL_BNC_31-5431.fab.gbr, AMPHENOL_BNC_31-5431.top.gbr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]
2019-02-08 Add: file describing the twinax polarity
    [twinax_doc.sch]
2019-02-12 Add: twinax connector to pcb-footprint needs solder mask clearnace fixed
    [bioamp.sch]
2020-03-24 add: went back through my notes to see about lower freq cutout and gain
    [bioamp.sch, output.sch]
2020-03-25 add: netnames and cleanup of output.sch
    [output.sch]
2020-03-26 add: notes to output.sch and proper values for gain and output stage
    [output.sch]
2020-03-26 add: notes on output stage servo and title block update to the current project
    [bioamp.sch, output.sch]
2020-03-26 add: note for tomorrow about alternative feeback point for servo
    [output.sch]
2020-03-26 add: revised to feedback into ref pin
    [bioamp.sch, output.sch]
2020-03-27 fix: all refdes are in order now and have a plan
    [bioamp.sch, output.sch]
2020-03-27 fix: servo is now set for 300Hz as the systems -3db point for high pass
    [bioamp.sch]
2020-04-23 add: imported stuff from cheap version that worked well (sch)
    [bioamp.sch, output.sch]
2020-04-25 fix: numerous small changes to footprints and netnames to match fancy vs cheap versions correctly
    [bioamp.sch, output.sch]
2020-04-25 add: improved architecture in the gain stage to make switch failure intrinsically safe
    [output.sch]
2020-06-02 add: mid stage opamp selected, minor drafting improvements
    [bioamp.sch, output.sch]
2020-06-02 fix: wrong opamp selection last time and fix to gains to match user spec.
    [output.sch]
2020-06-02 fix: polarity fixed
    [bioamp.sch]
2020-06-02 clean: cleaning of the old layout so I can play with component placement
    [output.sch]
2020-06-02 fix: import revised footprint for the twinax connector from the cheap version
    [bioamp.sch]
2020-06-02 add: minor fixes to schematic refdes and improvements to footprint placement
    [bioamp.sch, output.sch]
2020-06-04 add: minor tweeks to routing and a fix to the input polarity
    [bioamp-art.gbl, bioamp-art.gbo, bioamp-art.gbp, bioamp-art.gbs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]
2020-06-10 add: packaging for fancy version
    [bioamp-art.gbl, bioamp-art.gbo, bioamp-art.gbp, bioamp-art.gbs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]
2020-08-20 fix: corrections to the feedback capacitors
    [output.sch]
2020-08-21 add: first pass at adding connections for a powerline notch filter on a plugin card
    [output.sch]
2020-08-21 add: improved routing for the power line notch filter plugin card
    [output.sch]
2020-09-08 fix: change the connectors for the 60Hz notch filter addon
    [output.sch]
2020-09-08 fix: fancy version name and solder mask hole alignment
    [bioamp-art.gbl, bioamp-art.gbo, bioamp-art.gbp, bioamp-art.gbs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]
2020-09-08 fix: final packaging
    [bioamp-art.gbl, bioamp-art.gbo, bioamp-art.gbp, bioamp-art.gbs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]
2020-09-11 add: improved connection point for future proofing
    [bioamp-art.gbl, bioamp-art.gbo, bioamp-art.gbp, bioamp-art.gbs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]
2020-12-01 add: revised layout for AD8221 and cleanup
    [bioamp.sch, output.sch]
2020-12-10 fix: silk and mask corrections
    [bioamp-art.gbl, bioamp-art.gbo, bioamp-art.gbp, bioamp-art.gbs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]
2020-12-10 add: power connector silk screen pinout
2020-12-14 add: repackaged for release
    [bioamp-art.gbl, bioamp-art.gbo, bioamp-art.gbp, bioamp-art.gbs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]
2020-12-14 fix: hpf/servo resistor value fixes
    [bioamp.sch]
2020-12-15 fix: minor component changes
    [bioamp.sch]
2021-03-08 add: exported front panel for test printing
2021-03-09 fix: all controls now have the high and low settings on the same side
    [output.sch]
2021-03-09 add: updated printout files of the front panel
2021-03-09 add: updated date
    [bioamp.sch, output.sch]
2021-03-25 add: revised Tx01MHAV series switch footprints
    [output.sch]
2021-03-30 add: ferrite beads to the input path and better option board connector alignment.
    [bioamp.sch, notchfilter-alt.sch, notchfilter.sch, output.sch]
2021-04-01 Add: notes on capacitor selection
    [bioamp.sch, notchfilter-alt.sch, output.sch]
2021-04-01 cleanup: removing Twin T notch filter
    [notchfilter-alt.sch, notchfilter.sch]
2021-04-05 add: initial pcb layout for notch filter. caps need mask fixes
    [notchfilter.sch]
2021-04-05 Fix: capacitor footprints
2021-04-06 Add: packaging of notch option board
    [notchfilter-opt-art.gbl, notchfilter-opt-art.gbo, notchfilter-opt-art.gbp, notchfilter-opt-art.gbs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]
2021-04-06 Add: revised packaging for oshpark
    [bioamp-art.gbl, bioamp-art.gbo, bioamp-art.gbp, bioamp-art.gbs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]
2021-04-06 Add: Schematics in PNG and PS formats
    [bioamp.sch, notchfilter.sch, output.sch, twinax_doc.sch]
2021-04-07 Add: improved breakout pod
    [breakout.bottom_copper.gbl, breakout.bottom_mask.gbs, breakout.bottom_paste.gbp, breakout.bottom_silk.gbo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]
2021-04-07 fix: trying better outline for safelead pin
    [breakout.bottom_copper.gbl, breakout.bottom_mask.gbs, breakout.bottom_paste.gbp, breakout.bottom_silk.gbo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]
2021-04-07 add: vector back panel for dual 9V
2021-04-09 add: final pcb design
    [breakout.bottom_copper.gbl, breakout.bottom_mask.gbs, breakout.bottom_paste.gbp, breakout.bottom_silk.gbo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]
2021-04-09 add: export for oshpark and test printing
    [breakout.gbl, breakout.gbo, breakout.gbp, breakout.gbs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]
2021-04-09 Add: chassis to screw connection and silk text
2021-04-09 add: improved cam output
    [breakout.gbl, breakout.gbo, breakout.gbp, breakout.gbs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]
2021-04-20 add/fix: notes and correction about gain resistors and associated capacitors
    [breakout.gbl, breakout.gbo, breakout.gbp, breakout.gbs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]
2021-04-20 clean: old files
    [breakout.gbl, breakout.gbo, breakout.gbp, breakout.gbs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]
2021-04-28 add: high pass filter optional adjustment
    [bioamp.sch, highpass.sch, notchfilter.sch, output.sch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]
2021-04-28 add: extra footprints for padding components (because supply chains and covid)
    [bioamp.sch, notchfilter.sch, output.sch]
2021-04-28 fix: alignment of switch fronts to bnc connectors and pcb edge
2021-04-28 add: pcb layout for optional high pass filter adj
    [highpass.sch]
2021-04-28 add: improved outline and routing for a narrower high pass filter option pcb
2021-04-28 fix: notch filter interboard connectors are now on the bottom of the board
2021-04-28 add: minor improvements to text and refdes alginment
    [bioamp.sch, notchfilter.sch, output.sch]
2021-04-28 add: revised front panels for additional options, gains, and improved text for notch filter
2021-04-30 add: more in the bom for resistors
2021-04-30 add: yet more in the bom for capacitors
2021-05-03 add: space to hand write notch filter frequency on silk if needed
2021-05-03 add: minor fixes and packaging
    [bioamp-art.gbl, bioamp-art.gbo, bioamp-art.gbp, bioamp-art.gbs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]
2021-05-04 add: bom omitted subrack chassis housing
2021-05-04 add: 9V battery holder and connector housings to bom
2021-05-04 add: improved clearance on input bnc hole
2021-05-05 add: schematics for power supply options
    [batterypower.sch, bioamp.sch, highpass.sch, notchfilter.sch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]
2021-05-05 add: symbols for schematics for power supply options
2021-05-06 add: additiona footprint for one of the capacitors that's proving hard to source reliably
    [output.sch]
2021-05-06 add: schematics exported to ps and png
    [output.sch]
2021-05-06 add: revised makefile to include wire harness schematics
2021-05-10 add: revised note in readme about input connectors
2021-05-11 add: notes and the END of safelead adapters as connectors
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2021-05-11 add: improved layer use and export for printing
    [breakout.bottom_copper.gbl, breakout.bottom_mask.gbs, breakout.bottom_paste.gbp, breakout.bottom_silk.gbo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]
2021-05-12 add: changed output resistor to 100 ohms
    [output.sch]
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2021-11-12 add: block diagram
    [bioamp_block.sch]
2022-01-22 add: note about C40 and C41 for HPF 10Hz operation
    [bioamp.sch]
2022-03-24 add: test fixture
    [testfixture.sch]
2022-03-24 fix: updated page numbers
    [batterypower.sch, bioamp.sch, dipadapter.sch, highpass.sch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]
2022-03-24 fix: refdes correction to twisted pair wiring example diagram
    [twinax_doc.sch]
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2025-03-10 fix: readme pcb art link
2025-03-10 fix: readme pcb art link 2
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2025-03-11 fix: readme + schematic for input capacitors having dielectric absorbtion
    [bioamp-20250310.sch]
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2025-03-11 add: revision about unstuffed capacitors
    [notchfilter.sch]
2025-03-11 fix: syntax error in : revision about unstuffed capacitors
2025-03-11 fix: syntax error in2 : revision about unstuffed capacitors
2025-03-11 fix: syntax error in3 : revision about unstuffed capacitors
2025-03-11 fix: syntax error in4 : revision about unstuffed capacitors
2025-03-11 fix: omitted output.sch : revision about unstuffed capacitors
    [output.sch]
2025-03-11 fix: omitted output.sch : revision about unstuffed capacitors 2
2025-03-11 add: updated bioamp fancy gerbers for oshpark
    [bioamp-art.gbl, bioamp-art.gbo, bioamp-art.gbp, bioamp-art.gbs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]
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
